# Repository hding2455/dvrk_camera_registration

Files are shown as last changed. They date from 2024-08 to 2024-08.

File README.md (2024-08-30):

# dVRK hand-eye calibration package

A ROS package to perform camera registration for the dVRK robot.

**Setup notes**

This script was tested on ROS noetic and dVRK release 2.2.1+

On Ubuntu 20.04 you might need to compile `gscam` (see notes in `dvrk_video` package: https://github.com/jhu-dvrk/dvrk_video). You might also have to install scipy with pip3 in your user directory using `pip3 install --user scipy==1.4.0`.

# Introduction

The goal of this package is to perform hand-eye calibration between a dVRK PSM arm and the camera, ideally a stereo endoscope.  This can be especially useful for groups that don't have a full patient cart or a Setup Joint (SUJ) controller.  This script will tell you where the PSM is located with respect to the camera or ECM.  This will allow you to use the teleoperation components provided by the dVRK stack.  This code can also be used instead of the SUJ since the accuracy can be higher than the SUJs (SUJs are within 5cm cube reporting PSMs wrt ECM, the camera registration script seems to achieve an accuracy closer to 5mm to 10mm cube).
 
Most of the dVRK groups have an original endoscope and CCUs from Intuitive Surgical Inc with SDI outputs so we will assume a stereo camera even though this hand-eye calibration uses only one channel (mono).  The registration uses a small ArUco marker mounted on the shaft of the instrument (you can find an STL model for the mount in the `assets` directory as well as ArUco `.svg` files).  The ArUco marker can be removed once the registration is performed.  The overall steps are:
* Calibrate the camera
* Run the camera registration script
  * Manually move the PSM to safe locations to define the boundaries of the search space
  * The code will compute a convex hull based on the user provided poses
  * Let the code move the PSM around to collect data while not colliding with the environment
* Optionally, validate the results
* Copy-paste the resulting transformation to the dVRK console or your suj-fixed.json

There are two specific cases:
* Fixed camera.  In this case, the registration transformation can be used in your console.json to define the `base-frame`.
* Camera held by an ECM.  In this case, you should have a console.json that uses an SUJ of type `SUJ_Fixed`.  The SUJ has a "kinematic" configuration file  called `suj-fixed.json` by convention.  The result of the registration will need to be copy-pasted in this file.  Examples of configuration files using the Fixed SUJ can be found in https://github.com/dvrk-config/dvrk_config_jhu/tree/main/jhu-daVinci-Si.

The camera registration script will automatically save the correct transformation based on the `-e` command line option.  If you specify an ECM, the script assumes you are using a fixed SUJ.  Otherwise, it assumes you just need the PSM base frame for the console.json.

# Steps

## Create a catkin package

### Stereo

You will need to create a new package to store the calibration results.  At that point, choose a name for your camera (aka stereo rig).  For this example, we will use `jhu_daVinci`:
```bash
cd ~/catkin_ws/src
catkin_create_pkg jhu_daVinci
catkin build
source ~/catkin_ws/devel/setup.bash # you have a new package so you need to source again
```

### Mono

There is no difference but for sake of demonstration, we will create the package under a different name, say "depstech", a familiar brand of cheap USB cameras.
```bash
cd ~/catkin_ws/src
catkin_create_pkg depstech
catkin build
source ~/catkin_ws/devel/setup.bash # you have a new package so you need to source again
```

## Start the video

### Stereo

The following is based on dVRK provided launch files to capture the stereo video using Decklink SDI frame grabbers.  If your frame grabbers are different you will have to create your own launch files.  Note that you have to provide the name of your stereo rig:
```bash
roslaunch dvrk_video stereo_decklink_1280x1024.launch stereo_rig_name:=jhu_daVinci
```
### Mono

The following example is based on a video4linux compatible source:
```bash
roslaunch dvrk_video gscam_v4l.launch camera_name:=depstech
```

## Calibrate the camera

### Stereo

The calibration is performed using the ROS provided application, please refer to their documentation for the parameters (http://wiki.ros.org/camera_calibration).  You need to make sure the video stream is started and you are using the correct rig name.
```bash
rosrun camera_calibration cameracalibrator.py --approximate 0.1 --size 12x10 --square 0.0045 right:=/jhu_daVinci/right/image_raw left:=/jhu_daVinci/left/image_raw left_camera:=/jhu_daVinci/left right_camera:=/jhu_daVinci/right
```
The command line above assumes you're using a 12x10 calibration grid and the size of each square is 4.5mm.  Once the calibration is performed, don't forget to save and commit using the GUI.  You should now have two new files in the catkin package you created for the stereo rig under `calibrations`: `left.yaml` and `right.yaml`.

You can find some calibration checkerboards ready to print in the `assets` directory.  Make sure the scale is correct after printing.  The simplest solution is to measure 10 consecutive squares and verify that it's 10 times the claimed square size in mm.  Also to note, the checkerboard size (e.g. 12x10) is based on the number of corners between the squares.  For example, the 12x10 actually has 13x11 squares.

### Mono

The only difference is the parameters:
```bash
rosrun camera_calibration cameracalibrator.py --size 12x10 --square 0.0045 image:=/depstech/image_raw camera:=/depstech
```

## Restart the video using the calibration

At that point, you need to stop the launch file used for the video acquisition and restart it with the `stereo_proc` parameter set to `True`.  This will add a ROS node to compute the rectified images and publish the camera parameters needed for the camera registration.

### Stereo
```bash
roslaunch dvrk_video stereo_decklink_1280x1024.launch stereo_rig_name:=jhu_daVinci stereo_proc:=True
```

### Mono
```bash
roslaunch dvrk_video gscam_v4l.launch camera_name:=depstech mono_proc:=True
```

## Start the dVRK console

Start a dVRK console with the PSM you mean to register.  If you have an ECM and want to register it as well, you need a console file with at least the PSM you want to register as well as the ECM.  We strongly recommend to use a console.json file with no base frame set for the PSM and ECM.  If you're using the Fixed SUJ, make sure the transformations in `suj-fixed.json` are all set to identity.

## Hand-eye calibration script

To perform the hand-eye calibration, you need to attach the calibration ArUco marker to the PSM shaft, ideally about 70mm from the tip.  The exact position doesn't matter.  You can 3D print the ArUco mount provided in the `assets` directory to hold the ArUco marker.  You will need to tap the smaller hole and use a screw to push against the instrument's shaft.

The `camera_registration.py` script first asks the user to move the PSM to create a convex hull in which it is safe to move.  During this stage, the PSM should be powered and you can use the clutch button to free the arm.  Move the tip without worrying if the ArUco marker is visible and try to create the largest volume possible in front of the camera.  When you're done, place the PSM so the ArUco marker is facing the camera and is close to the center of the volume you just created.  The script will then move the robot automatically to collect data for the hand-eye calibration.  To run the script:
```bash
rosrun dvrk_camera_registration camera_registration.py -p PSM2 -m 0.01 -c /jhu_daVinci/left
```
`-p` is used to indicate which PSM to use and `-c` is the namespace for your camera.  If you also have an ECM, add `-e ECM`:
```bash
rosrun dvrk_camera_registration camera_registration.py -p PSM2 -m 0.01 -c /jhu_daVinci/left -e ECM
```

After collecting the data, the script will generate a couple of `.json` files with the transformation between the PSM and the camera.  The file with `-open-cv` is used for the validation script below.

## Validation script

We also provide a  script that overlays the estimated pose of the PSM end-effector based on the telemetry.  You can run this script right after the camera registration.  Make sure the video is still running with `stereo_proc` set to `True`.
```bash
rosrun dvrk_camera_registration vis_gripper_pose.py -p PSM2 -c /jhu_daVinci/left -H PSM2-registration-open-cv.json
```

## Edit your dVRK configuration files

If you don't have an ECM (i.e., a fixed camera), the registration script creates a `PSM<x>_registration-dVRK.json` file that contains a transformation you can copy-paste in your dVRK `console.json` to define the PSM `base-frame`.  If you have an ECM, the content of `PSM<x>_registration-dVRK.json` needs to be copy-pasted in the kinematic file for the Fixed SUJ (aka `suj-fixed.json`).

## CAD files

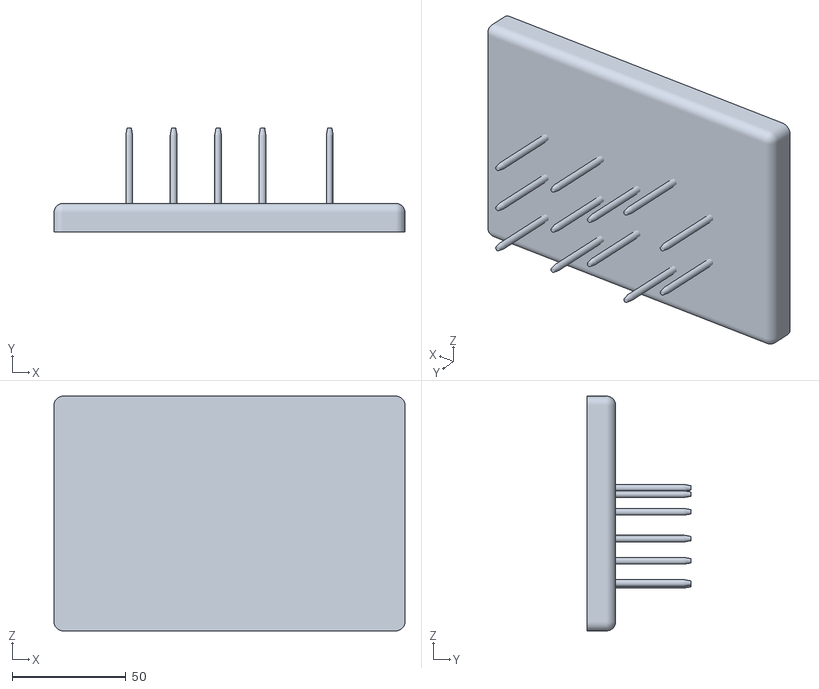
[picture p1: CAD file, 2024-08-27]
assets/assemblyboard.STL
154.0 x 45.5 x 103.0

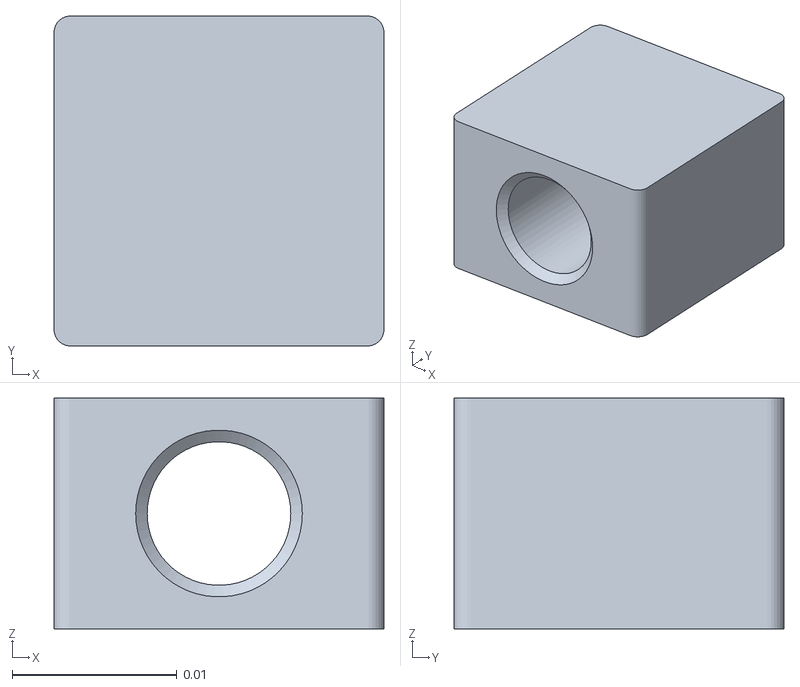
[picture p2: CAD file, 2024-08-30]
assets/PSM-Tracker-Mount.stl
0.02 x 0.02 x 0.014

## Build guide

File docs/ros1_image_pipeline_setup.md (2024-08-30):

# Setting ROS1 Image pipeline 

The following document describes how to set up some required features from the [ROS1 image pipeline][1] needed to use the hand-eye calibration script. Three steps need to be performed: (1) calibrating cameras, (2) publishing calibration parameters in `camera_info` topic, and (3) undistort and republish frames.

[1]: https://wiki.ros.org/image_pipeline

## Step 1: print calibration checkerboard

Print checkerboard from here: <https://github.com/Cartucho/dvrk_calib_hand_eye/blob/main/camera_calibration.md>.  This pattern has the following features:
* Square size: 4.80mm -> 0.00480m
* Size: 22x17

Check the printer has not scaled the checkerboard by measuring the square size. Other patterns can be used but the `square_size` and the `size` are needed when calling the calibration scripts.

## Step 2: Create package to store camera calibrations

Before launching your video pipeline, you should create a package to store the camera calibration parameters. Make sure that the name of your package is the same as the `rig_name` defined in your launch file. You can create a package with the following commands:

```bash
cd ~/catkin_ws/src
catkin_create_pkg <rig_name>
cd ~/catkin_ws
catkin build
source ~/catkin_ws/devel/setup.bash
```

Then launch the file with

```bash
roslaunch dvrk_camera_registration jhu_daVinci_video.launch
```

Make sure that you are not getting warnings such as

```
[ WARN] [1713557429.852579673]: unknown package: jhu_daVinci_endoscope_calibration (ignored)
```

This implies that the package was not found in the workspace. Try to rebuild the workspace with `catkin build`, source the workspace again, and the relaunch the video launch file.

## Step 2: Camera calibration 

```
rosrun camera_calibration cameracalibrator.py --approximate 0.1 --size 12x10 --square 0.0045 right:=/jhu_daVinci/right/image_raw left:=/jhu_daVinci/left/image_raw right_camera:=/jhu_daVinci/right left_camera:=/jhu_daVinci/left
```

After calibration, click on the commit button to save your calibrations in the package that was created in the previous step.

### Deprecated (See what should be kept in the final version of the documentation)
Camera calibration can be performed with any software that generates the standard 3x3 camera intrinsics and 1x5 distortion coefficients specified in OpenCV. Since the hand-eye calibration expects the parameters to be published in a standard ROS topic, it is recommended to use ROS utils to calibrate the cameras.

Monocular calibration (Single camera)
```bash
rosrun camera_calibration cameracalibrator.py --size 22x17 --square 0.0048 image:=/jhu_daVinci/left/decklink/jhu_daVinci_left/image_raw camera:=/jhu_daVinci/left/decklink/jhu_daVinci_left/ --no-service-check
```

Stereo calibration (Camera pair)
```bash
rosrun camera_calibration cameracalibrator.py --approximate 0.1 --size 22x17 --square 0.0048 right:=/jhu_daVinci/decklink/right/image_raw left:=/jhu_daVinci/decklink/left/image_raw right_camera:=/my_stereo/right left_camera:=/my_stereo/left --no-service-check
```

After running the calibration GUI make sure to save the calibration parameters. The application will create a compressed file with the pictures used for calibration and a `yaml` file with the actual parameters. 

### Checking the calibration's quality
After generating the camera parameters, hold the calibration board in front of the camera again to see the epipolar error. According to [ROS documentation][epipolar_error] this error should be ideally below 0.1 pixels. The best error I was able to obtained with an old dVRK endoscope was around 1.3 pixels. Handeye calibration is very sensitive to bad calibrations.

[epipolar_error]: <https://wiki.ros.org/camera_calibration/Tutorials/StereoCalibration#:~:text=Typically%2C%20an%20epipolar%20error%20below,acceptable%2C%20and%20below%200.1%20excellent>

<details>
  <summary>ROS camera calibration utils documentation</summary>
  
* [Camera calibration in ros](https://wiki.ros.org/camera_calibration)
* [Monocular calibration](https://wiki.ros.org/camera_calibration/Tutorials/MonocularCalibration)
* [Stereo calibration](https://wiki.ros.org/camera_calibration/Tutorials/StereoCalibration)
</details>

## Step 3 - Modify video launch files 

Modify the video launch file so that correct camera parameters are published in `camera_info` topic. To do this extract the .yaml file generated by the calibration script and add the location of this file to the video [pipeline launch file](../video_launch_files/jhu_daVinci_video.launch).

```xml
<arg name="camera_info_file" value="file:////home/jbarrag3/research_juan/hand_eye_collect/data_ros_calib/stereo_calib1/right.yaml"/>
```

Modify this file for both left and right cameras.

<details>
  <summary> Image info publisher documentation</summary>

* [Image publisher](https://wiki.ros.org/image_publisher?distro=noetic)
* [Camera info](https://wiki.ros.org/image_pipeline/CameraInfo)
* [Publishing parameters with a script](https://gist.github.com/rossbar/ebb282c3b73c41c1404123de6cea4771)
</details>

## Step 4: Rectify (undistorted) images 

Images can be rectified, i.e., undistorted with the `stereo_image_proc` function in the `image_pipeline`

```bash
ROS_NAMESPACE=/jhu_daVinci/decklink/ rosrun stereo_image_proc stereo_image_proc
```

After running this script you should obtain an `image_rect_color` topic for your left and right cameras.

```
rosrun image_view image_view image:=/jhu_daVinci/decklink/left/image_rect_color
```

<details>
  <summary>Image processing documentation</summary>

* [Monocular image proc](https://wiki.ros.org/image_proc)
* [Stereo image proc](https://wiki.ros.org/stereo_image_proc)

</details>

<details>
  <summary> Trouble shooting the image processor </summary>

The ROS image processing package expects the topics in a very specific format to process the pair of stereo images. If you are using a different launch file than the one provided in this repo check that the topics have the right format

```bash
rostopic list | grep image_raw$
```

This command should result in 
```bash
/jhu_daVinci/decklink/left/image_raw
/jhu_daVinci/decklink/right/image_raw
```
</details>

## Additional resources

* <https://jeffzzq.medium.com/ros2-image-pipeline-tutorial-3b18903e7329>
* <https://crtk-robotics.readthedocs.io/en/latest/pages/clients.html#>

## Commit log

2024-08-27 add assets
    [assemblyboard.STL]
2024-08-30 no idea
    [PSM-Tracker-Mount.stl, assemblyboard.STL]
